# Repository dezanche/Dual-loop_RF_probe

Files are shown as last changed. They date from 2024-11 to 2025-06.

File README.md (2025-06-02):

# Decoupled Dual-Loop RF Magnetic Field Probe
 

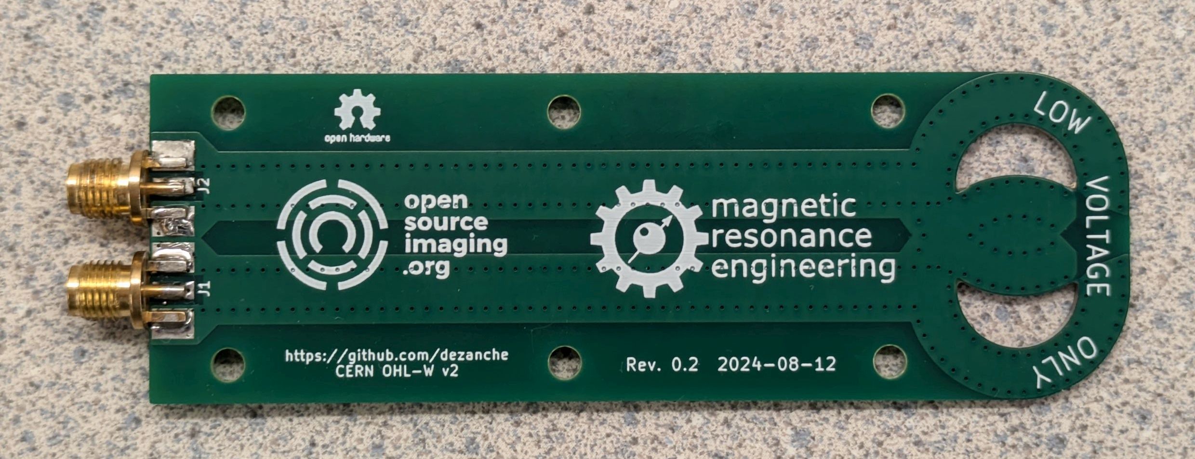
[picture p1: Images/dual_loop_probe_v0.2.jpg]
board photo


## MRI and RF Coils
Magnetic resonance imaging (MRI) requires radio frequency (RF) “coils” to excite and receive the MR signal from <sup>1</sup>H nuclei (protons). Coils are similar to antennas: they must produce a desired field pattern and operate at a given frequency, which for MR is known as the Larmor frequency and is given by the product of the scanner’s static magnetic field (B<sub>0</sub> in tesla – T) and gyromagnetic ratio (γ = 42.58 MHz/T for protons) of the nuclei.

## Measurement of Resonant Frequency and Q

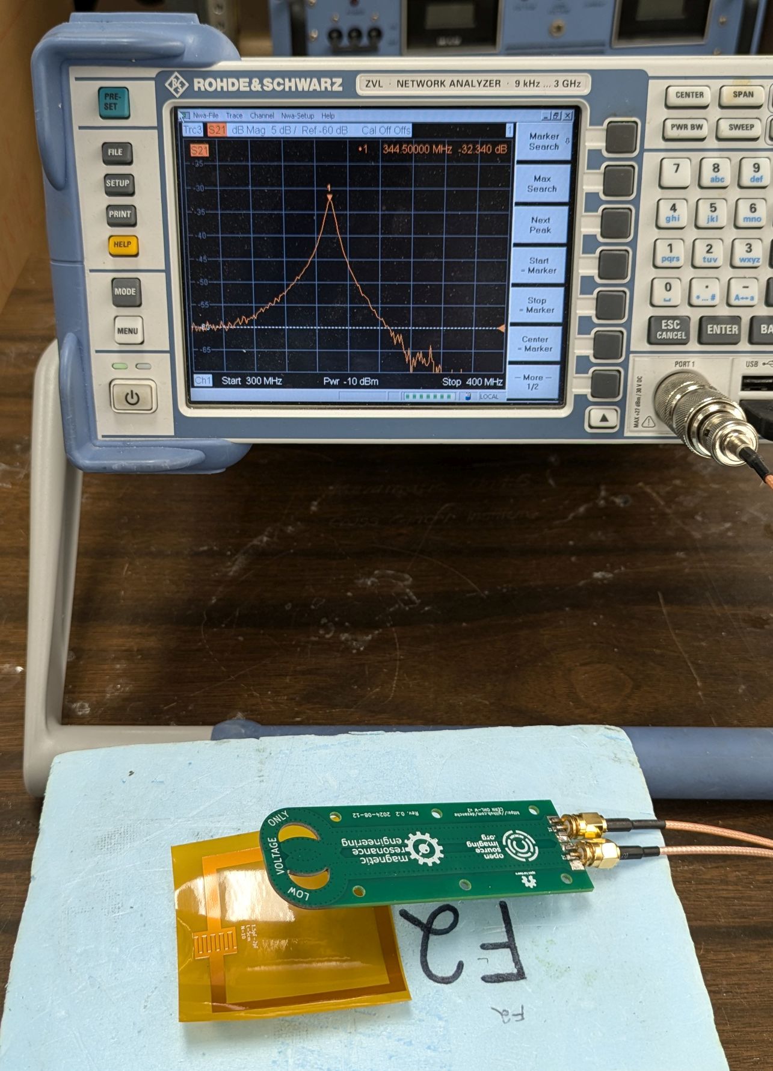
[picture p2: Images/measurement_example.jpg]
measurement photo


To achieve optimal performance, coils must usually be tuned to the Larmor frequency, e.g., by adjusting one or more capacitors or physical dimensions. Resonant frequency can be measured readily using a vector network analyzer (VNA) and a [single loop probe](https://github.com/dezanche/H-field_RF_probe/) with an S<sub>11</sub> measurement (analogous to the dip meter measurement used in the past when VNAs were not cheap and portable). 
The coil’s sensitivity or SNR of the received signal is related to the ratio of loaded and unloaded quality factors (Q) [1]. With some corrections [2], Q can be measured using the same S<sub>11</sub> measurement above, but it is challenging because the correction depends on the strength of the coupling which is difficult to control, especially if the probe is positioned manually. It is much more convenient to use two probes and an S<sub>21</sub> measurement, in which case the Q is simply f<sub>0</sub>/∆f, where f<sub>0</sub> is the center frequency and ∆f is the FWHM of the resonance curve as shown below.

resonance curve

For this 2-probe measurement it is important that, in absence of the coil being tested, the coupling (or crosstalk) between the two pickup loops be as small as possible (i.e., coupling through the coil should dominate). One way to achieve this is to position the pickup loops at opposite ends of a surface coil as shown below (left). However, this strategy will not work for all coil geometries, e.g., if the coil is small, or to measure the resonance of small accessory circuits like detuning traps.

coil Q measurement

Following the work of Darrasse and Kassab [3], it has become common to overlap the two pickup loops so that their mutual inductance is zero (right). Arranging the loops orthogonally is also a means of minimizing coupling [4]. It is common to make the pickup loops by hand using semi-rigid, hand-formable or flexible coaxial cable (https://www.uniteng.com/neildocs/references/Probing_the_Magnetic_Field_Probe.htm), but attaching them firmly together in the optimal position is often awkward and unreliable. Recently, a correction strategy was developed to compensate for any remaining coupling [5], but for the correction to work the coupling must remain constant in time.

## Design
The motivation for this work was to make a double-loop probe that is rugged, reliable and provides consistent and sufficiently low intrinsic coupling. The design follows the principles of the single [printed shielded loop probe](https://github.com/dezanche/H-field_RF_probe/), and uses a 4-layer PCB stackup in which the top and bottom layers are ground planes, while the two inner layers contain two stripline loops with appropriate overlap to minimize coupling.

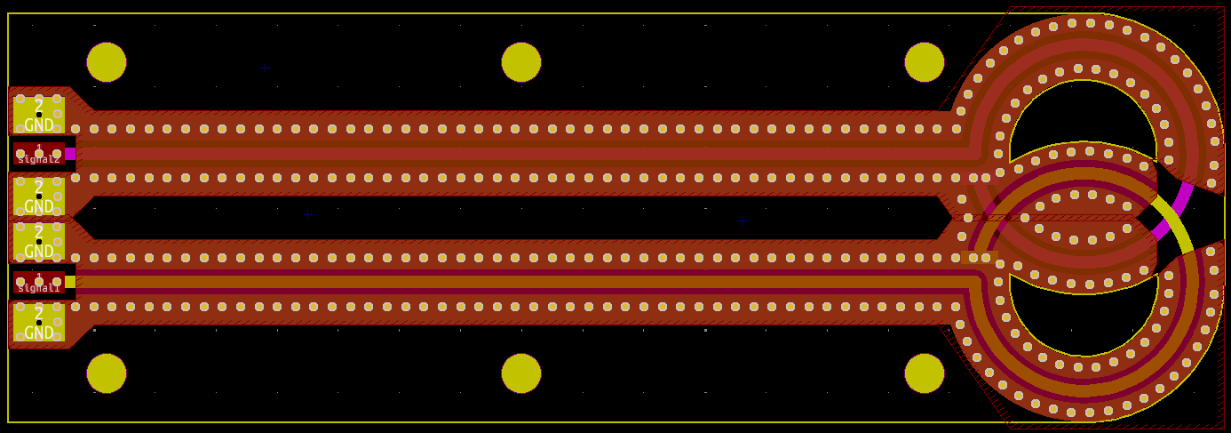
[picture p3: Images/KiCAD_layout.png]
4-layer PCB stackup


Connections from the board to coaxial cables are made at the end opposite the loops through two side-launch connectors such SMA (compatible with 1.6-mm-thick PCB). The PCB design is provided in both [KiCAD](https://www.kicad.org/) and Gerber format.

## Bill of Materials

| component | source | quantity | unit cost | total cost |
| --------- | ------ | -------- | --------- | ---------- |
| PCB  | various | 1 | 1 USD | 1 USD |
| RF connector | various | 2 | 1 USD | 2 USD |

Total cost of the dual-loop probe with connectors is about 3 USD and varies depending on board manufacturer as well as the type (SMA, QMA, SMB, etc.) and source of the RF connectors.

## Results
The probe was printed using 1.6-mm-thick FR4 material and standard manufacturing tolerances.
The isolation measured between the two ports in absence of other circuits or materials near the probe quantifies its baseline performance. Isolation is better than 50 dB up to 500 MHz, and the worst value up to 1 GHz is 38dB. Some adjustment of isolation is possible by removing small areas of the ground planes at the notch where the two loops cross over each other.

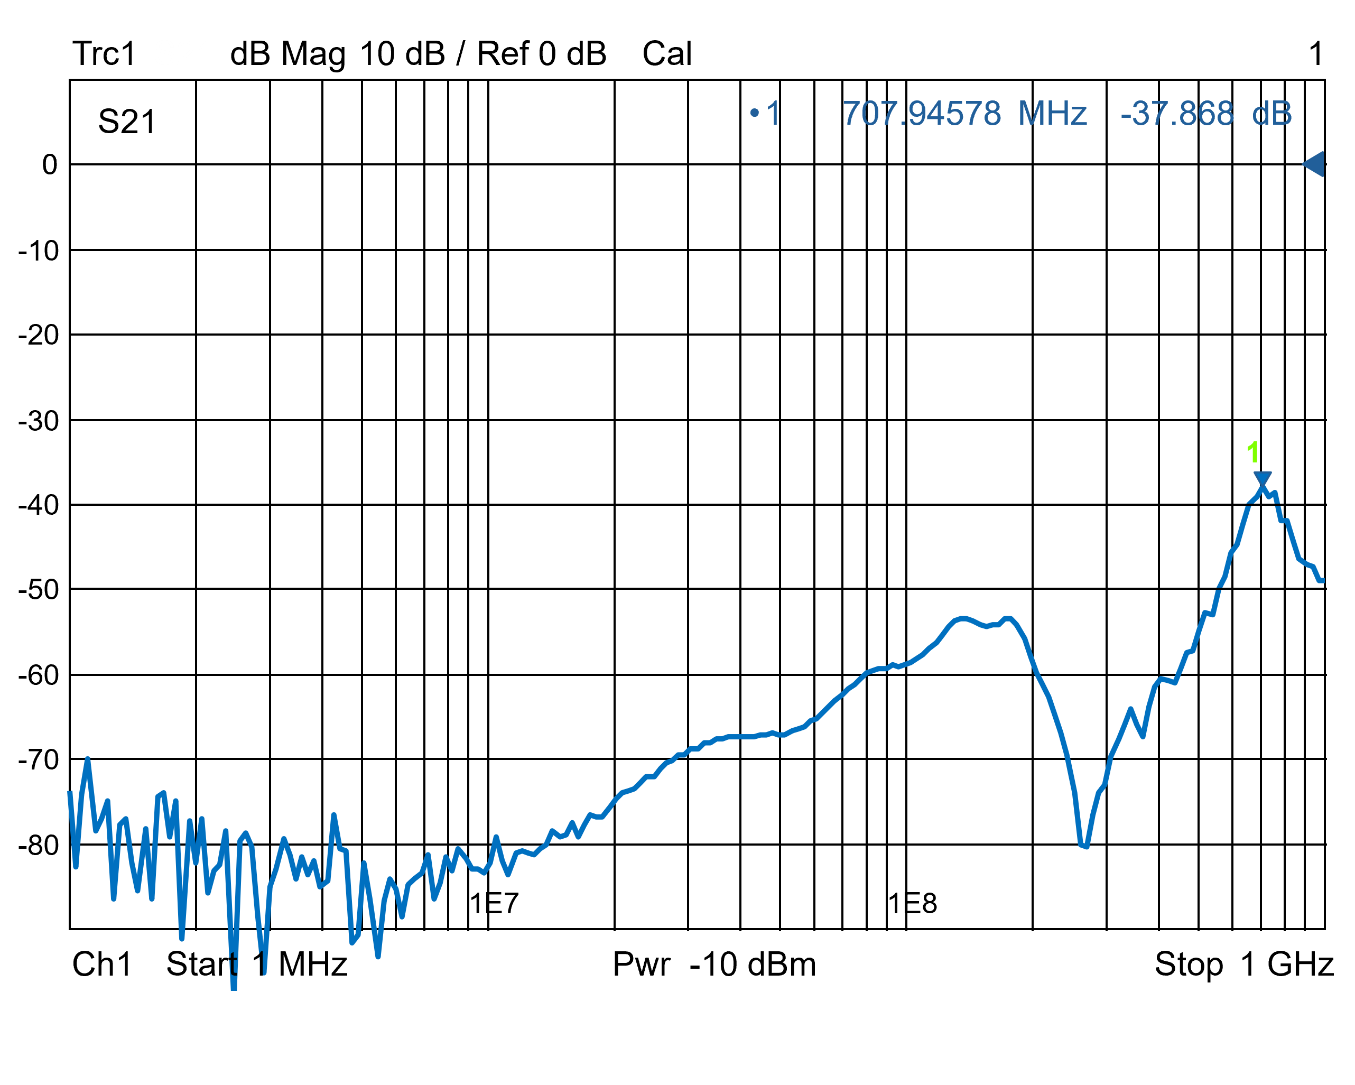
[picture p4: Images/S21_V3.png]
isolation


## Publications
A version of this work was presented at the [2025 meeting of the ISMRM](https://www.ismrm.org/25m/) (program #4402) and published as a hardware article in [HardwareX](https://doi.org/10.1016/j.ohx.2025.e00659).

## References
[1]	W. A. Edelstein, G. H. Glover, C. J. Hardy, and R. W. Redington, “The Intrinsic Signal-to-Noise Ratio in NMR Imaging,” Magn Reson Med, vol. 3, no. 4, pp. 604–618, 1986, doi: 10.1002/mrm.1910030413.

[2]	J. R. Ashley and F. M. Palka, “Reflection Coefficient Measurement of Microwave Resonator Q Factors,” The Microwave Journal, pp. 35–39, Jun. 1971.

[3]	Luc Darrasse and Ghazi Kassab, “Quick Measurement of NMR-Coil Sensitivity with a Dual-Loop Probe,” Review of Scientific Instruments, vol. 64, no. 7, pp. 1841–1844, Jul. 1993.

[4]	Axel Haase et al., “NMR Probeheads for In Vivo Applications,” Concepts in Magnetic Resonance, vol. 12, no. 6, pp. 361–388, 2000.

[5]	W. Wang, J. D. Sánchez-Heredia, T. Maurouard, V. Zhurbenko, and J. H. Ardenkjær-Larsen, “Calibrating Double-Loop H-Field Probe Measurements of RF Coil Current for MRI,” IEEE J. Electromagn. RF Microw. Med. Biol., vol. 7, no. 3, pp. 266–272, Sep. 2023, doi: 10.1109/JERM.2023.3274742.

## Contributors
Nicola De Zanche

Giulio Giovannetti

If you use this probe in your work, please cite the [Publications](#Publications) and this repository as described in the [CITATION](CITATION.cff) file.

## Licenses
Layouts and other CAD files are licensed under the [CERN-OHL-W 2.0 license](https://cern-ohl.web.cern.ch/), version 2.0 or any later version.\
\
All other original content in this repository (including this README file) is licensed under a [Creative Commons Attribution-NoDerivatives 4.0 International License](https://creativecommons.org/licenses/by-nd/4.0/).

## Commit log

2024-04-22 board preview
2024-11-07 update to version 0.2
    [dual_loop_probe-NPTH-drl_map.gbr, dual_loop_probe-PTH-drl_map.gbr, dual_loop_probe_0.2-B_Cu.gbr, dual_loop_probe_0.2-B_Mask.gbr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]
